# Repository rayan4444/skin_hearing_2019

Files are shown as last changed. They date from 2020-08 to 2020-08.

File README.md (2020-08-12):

# Skin Hearing PCB Repository

Altium files Repository for Skin Hearing project. The Main Board houses the microcontroller and options for audio inputs. The Flex Electrodes is a two-way configurable flex PCB for skin stimulating electrodes.

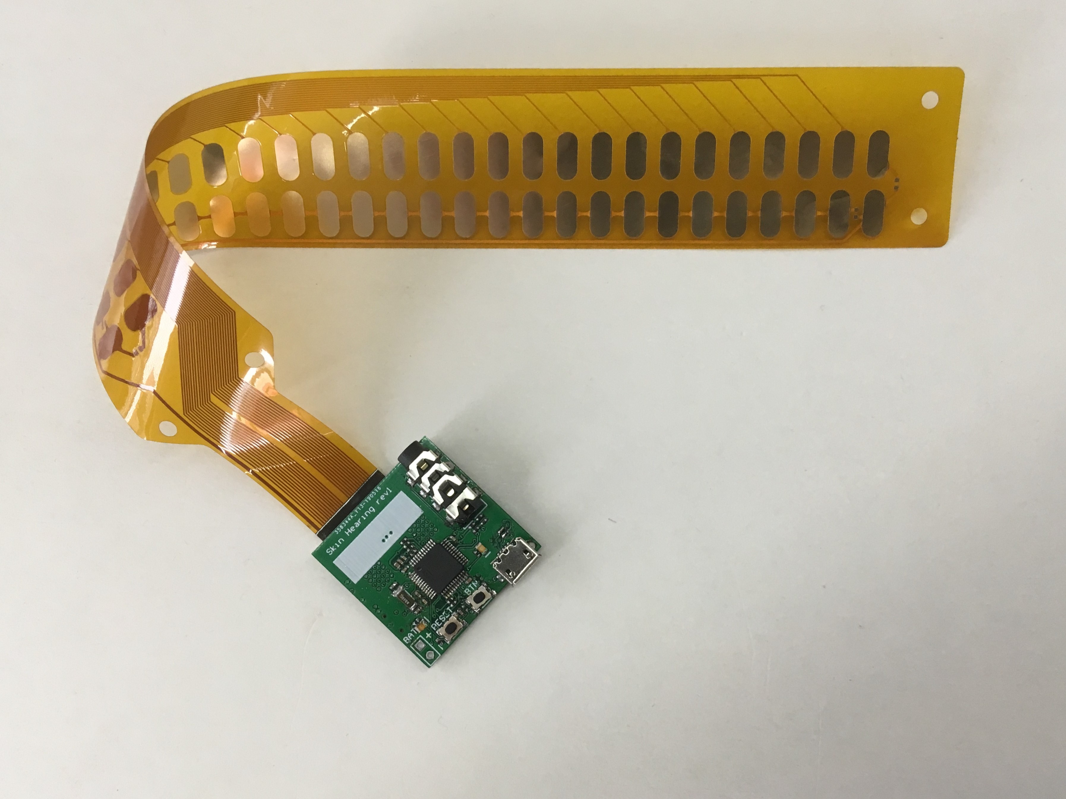
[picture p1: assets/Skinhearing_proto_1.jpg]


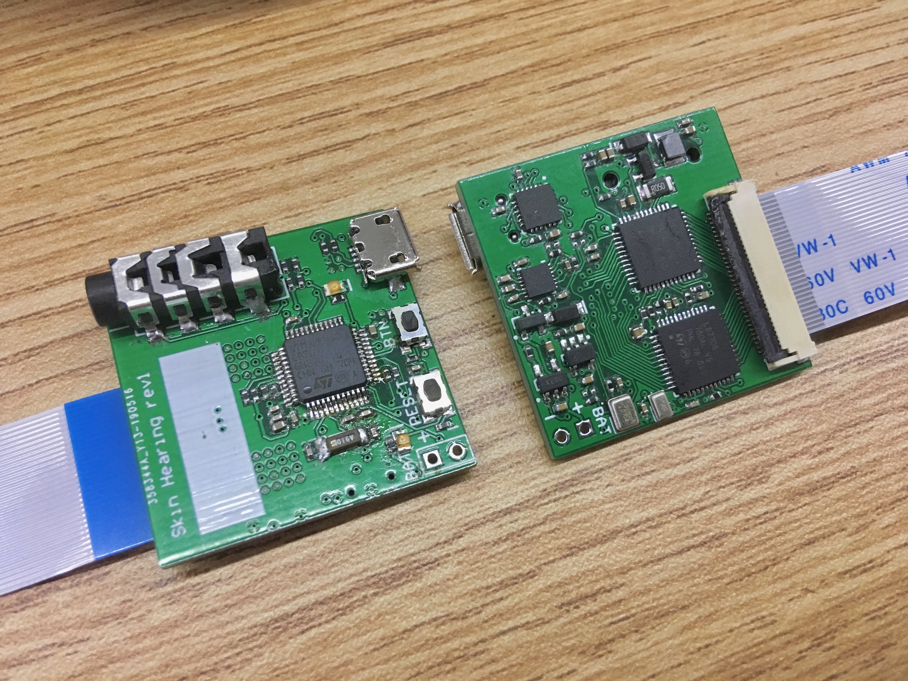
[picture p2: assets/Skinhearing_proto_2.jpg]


## Features
Main board: 4 Layers
* STM32F410 microcontroller
* 1x CP2104 USB-UART bridge
* 1x SPH0645LM4H-B Digital microphone
* 1x SPV1840LR5H-B Analog microphone
* 1x MAX9814 Audio amplifier
* 1x 3.5mm audio jack for external microphone
* 2x LED7708 LED drivers to control electrode current
* 1x 32pin FCC connector for electrodes
* 1x Button
* 1S Battery charger and LDO

Flex Electrodes:
* Configuration 1: solder 0Ω resistors on R3 and R2, leave R1 and R4 not populated
* Configuration 2: solder 0Ω resistors on R1 and R4, leave R2 and R3 not populated

## Connections and Pinout
STM32F410:

|Signal|Pin|Notes|
|:---:|:----:|:---:|
|USART1_TX|PA9|Programming|
|USART1_RX|PA10|Programming|
|Button|PA0||
|MIC_AMP|PB0|output of audio amplifier|
|I2S1_WS|PA4|digital mic|
|I2S1_CK|PA5|digital mic|
|I2S1_SD|PA7|digital mic|
|LE|PB12|LED driver|
|DCLK|PB13|LED driver|
|DOUT|PB14|LED driver|
|DIN|PB15|LED driver|
|GSSY|PA8|LED driver|
|XFLT|PA11|LED driver|
|IOK|PB5|LED driver|
|XVOK|PB6|LED driver|
|XOVF|PB7|LED driver|
|XMSK|PB8|LED driver|

## Programming instructions

1. Download and install [CP210x drivers](https://www.silabs.com/products/development-tools/software/usb-to-uart-bridge-vcp-drivers)
2. 	Make sure the BOOT config resitors are soldered properly to program over UART
BOOT0= HIGH, BOOT1=LOW
    * R18 and R23 soldered
    * R19 and R21 not populated
3. Get [STM32 flasher](https://www.st.com/en/development-tools/flasher-stm32.html) from the ST Website
4. Make sure your USB cable has communication wires!

## Firmware
Did not get consent to share

## Errata, fixes and debugging notes

#### Changes from rev 1.0
*	Removed R7 and R8 to improve USB reliability
* Corrected TX/RX connection on the CP2104 Chip
* Added Ground connections to the FPC connector
* Renamed channels to match the electrodes Flex PCB

#### Manufacturing notes
* Main board: 4L, 1.6mm thickness, 30x30mm

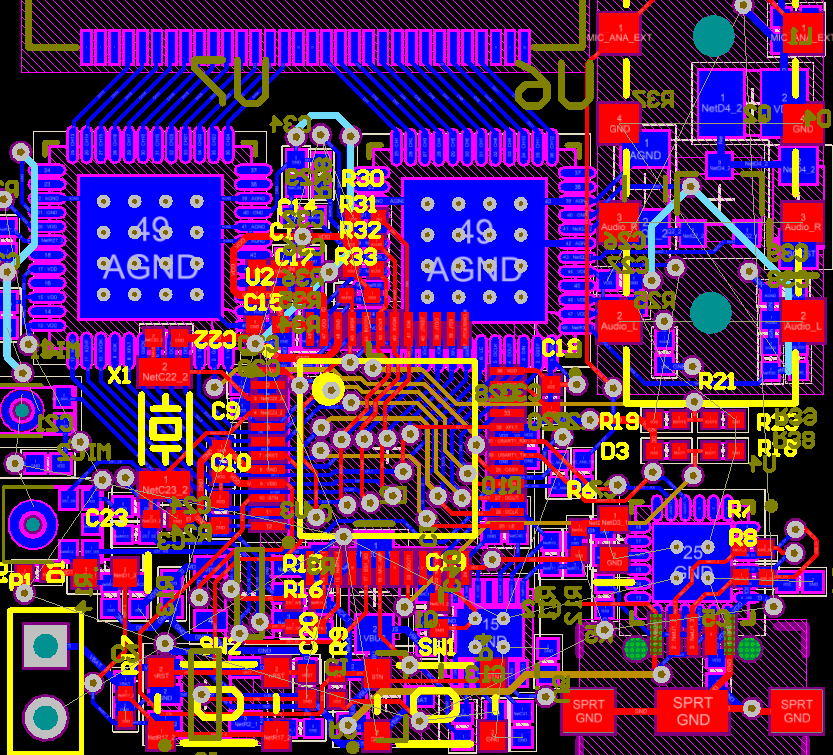
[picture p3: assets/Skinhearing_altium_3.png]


* Electrodes: FPC. See layer stack-up below

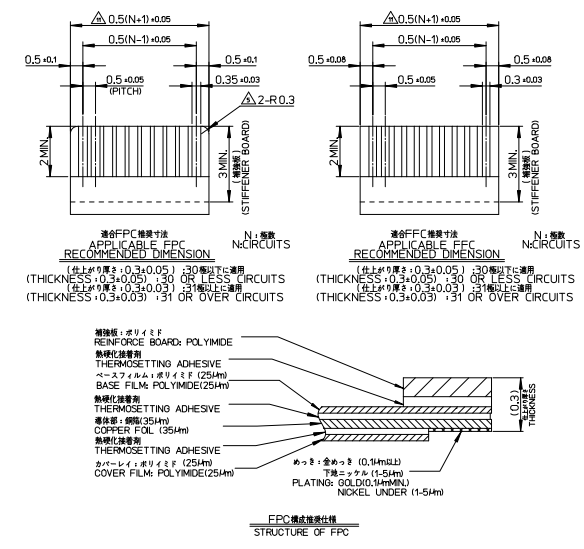
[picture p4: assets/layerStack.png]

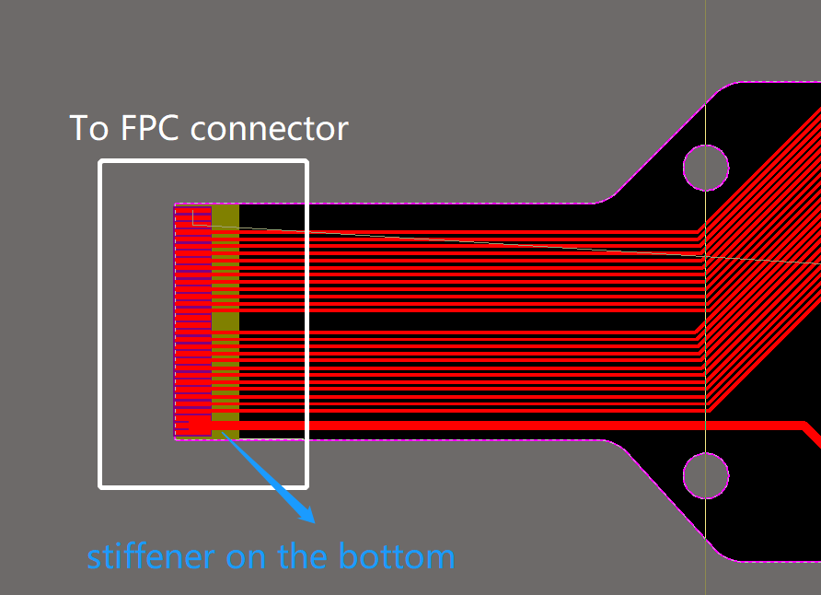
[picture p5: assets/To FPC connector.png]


#### Suggestions for future designs
*	Industrial design considerations: position of buttons, LED and connectors
* In case LED drivers produce discomfort: consider using a DAC and an improved Howland current pump to control the outputs to the electrodes.
* Remove redundant audio input source once you've tested all of them
* Consider communication with other devices: ex: Bluetooth

## Datasheets
* [LED7708](https://www.st.com/resource/en/datasheet/led7708.pdf)
* [MAX9814](https://datasheets.maximintegrated.com/en/ds/MAX9814.pdf)
* [STM32F410 - 48Pin](https://www.st.com/resource/en/datasheet/stm32f410cb.pdf)
* [SPV1840LR5H-B](https://www.knowles.com/docs/default-source/model-downloads/spv1840lr5h-b-rev-b-datasheet.pdf)
* [SPH0645LM4H-B](https://cdn-shop.adafruit.com/product-files/3421/i2S+Datasheet.PDF)
* [CP2104](https://www.silabs.com/documents/public/data-sheets/cp2104.pdf)

## References and Tutorials
* Examples for LED7708 firmware : [evaluation boards](https://www.st.com/content/st_com/en/products/evaluation-tools/solution-evaluation-tools/led-and-general-lighting-solution-eval-boards/steval-ill035v1.html#resource) and [software](https://www.st.com/content/st_com/en/products/evaluation-tools/solution-evaluation-tools/led-and-general-lighting-solution-eval-boards/steval-ill035v1.html#tools-software)
* [STM32F4 tutorials](http://stm32f4-discovery.net)

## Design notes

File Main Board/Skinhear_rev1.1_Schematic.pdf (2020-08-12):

# C11470nF C¹²

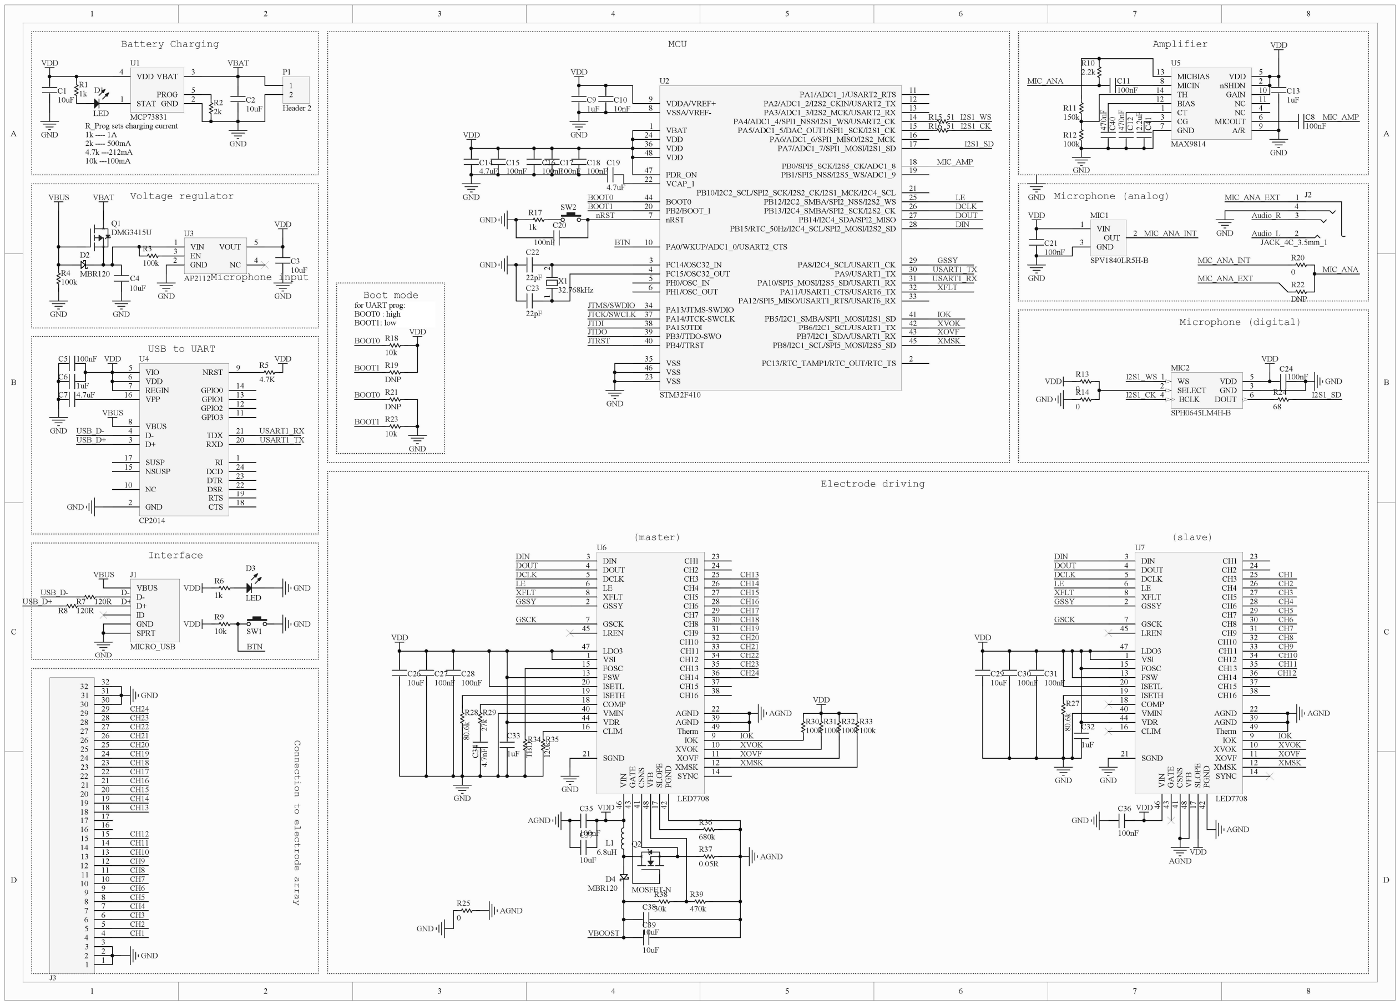
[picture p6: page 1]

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
### Battery Charging

### Voltage regulator

### Microphone input

### MCU

### Interface

STAT 1 | GND | 2
VBAT | 3 VDD 4
PROG | 5

U1

MCP73831

1k

R1

2k

R2 10uF

C1

10uF

C2

VDD | VBAT

GND

R_Prog sets charging current 1k ---- 1A
2k ---- 500mA
4.7k ---212mA
10k ---100mA

D1

LED

GND

1
2

P1

Header 2

10uF

C4

10uF

100k | C3

R3

GND

GND

GND

VDD

VBUS

100k

R4

GND

D2

MBR120

VBAT

Q1
DMG3415U
VIN 1

GND 2

EN 3
NC | 4
VOUT | 5

U3

AP2112

VBUS

GND

USB_D-USB_D+

RI 1

GND 2

D+ 3

D- 4

VIO 5
VDD 6
REGIN 7

VBUS 8

NRST 9

NC 10

GPIO3 | 11 GPIO2 | 12 GPIO1 | 13 GPIO0 | 14

NSUSP 15

VPP 16

SUSP 17

CTS | 18 RTS | 19
RXD | 20 TDX | 21
DSR | 22 DTR | 23 DCD | 24

U4

CP2014

1uF

C6

C7 4.7uF

C5 100nF

4.7K

R5

### USB to UART

VDD | VDD

GND

GND

R7 120R
R8 120R

USB_D-USB_D+

VBUS

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
VDD | GND

BTN

SW1

VBAT 1

PC13/RTC_TAMP1/RTC_OUT/RTC_TS 2

PC14/OSC32_IN 3
PC15/OSC32_OUT 4
PH0/OSC_IN 5
PH1/OSC_OUT 6

nRST 7

VSSA/VREF- 8

VDDA/VREF+ 9

PA0/WKUP/ADC1_0/USART2_CTS 10

PA1/ADC1_1/USART2_RTS | 11
PA2/ADC1_2/I2S2_CKIN/USART2_TX | 12
PA3/ADC1_3/I2S2_MCK/USART2_RX | 13
PA4/ADC1_4/SPI1_NSS/I2S1_WS/USART2_CK | 14
PA5/ADC1_5/DAC_OUT1/SPI1_SCK/I2S1_CK | 15
PA6/ADC1_6/SPI1_MISO/I2S2_MCK | 16
PA7/ADC1_7/SPI1_MOSI/I2S1_SD | 17
PB0/SPI5_SCK/I2S5_CK/ADC1_8 | 18
PB1/SPI5_NSS/I2S5_WS/ADC1_9 | 19

PB2/BOOT_1 20

PB10/I2C2_SCL/SPI2_SCK/I2S2_CK/I2S1_MCK/I2C4_SCL 21 VCAP_1 22

VSS 23

VDD 24

PB12/I2C2_SMBA/SPI2_NSS/I2S2_WS | 25
PB13/I2C4_SMBA/SPI2_SCK/I2S2_CK | 26
PB14/I2C4_SDA/SPI2_MISO | 27
PB15/RTC_50Hz/I2C4_SCL/SPI2_MOSI/I2S2_SD | 28
PA8/I2C4_SCL/USART1_CK | 29
PA9/USART1_TX | 30
PA10/SPI5_MOSI/I2S5_SD/USART1_RX | 31
PA11/USART1_CTS/USART6_TX | 32
PA12/SPI5_MISO/USART1_RTS/USART6_RX | 33
PA13/JTMS-SWDIO 34
PA14/JTCK-SWCLK 37
PA15/JTDI 38
PB3/JTDO-SWO 39
PB4/JTRST 40
PB5/I2C1_SMBA/SPI1_MOSI/I2S1_SD | 41
PB6/I2C1_SCL/USART1_TX | 42
PB7/I2C1_SDA/USART1_RX | 43

VSS 35

VDD 36

BOOT0 44

PB8/I2C1_SCL/SPI5_MOSI/I2S5_SD 45

VSS 46

PDR_ON 47

VDD 48

U2

STM32F410
GND

GND

JTMS/SWDIO
JTCK/SWCLK
JTDI
JTDO
JTRST
VDD | GND

4.7uF

C14

10nF

C10

4.7uF

C19

1uF

C9

VDD

100nF

C15
100nF

C16
100nF

C17
100nF

C18

BOOT0
BOOT1

BOOT0

BOOT1

BOOT0

BOOT1

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
Boot mode | 1 2 | X1
| | 32.768kHz

22pF

C22

22pF

C23

SW2
GND
1k
R17 | nRST

GND

BTN

USART1_TX
USART1_RX

100nF

C20

for UART prog:
BOOT0 : high
BOOT1: low | Microphone (digital)

### Microphone (analog)

### Amplifier

VDD

VDD

100nF

C24

68

R24

I2S1_WS
I2S1_CK

I2S1_SD

I2S1_CK | I2S1_SD
I2S1_WS | GND

R16 51

R15 51

VIN 1

GND 3

OUT 2

MIC1

SPV1840LR5H-B

VDD

GND

100nF

C21

GND | 3
DOUT | 6
VDD | 5

BCLK 4

SELECT 2 WS 1

MIC2

SPH0645LM4H-B

MIC_ANA_INT

1

3

2

4

J2

JACK_4C_3.5mm_1

MIC_ANA_EXT

GND Audio_L Audio_R

100nF

C8

0

R20

DNP

R22

MIC_ANA_EXT

MIC_ANA_INT

MIC_ANA

GND

100nF

GND

VDD

MIC_ANA

MIC_AMP

### Electrode driving

DIN
DOUT
DCLK
LE
XFLT
GSSY

GND

GND

100nF

C2880.6k

R28

# GND 27k

R29 4.7nFC³⁴ | 1uF
C33 | 120k
R35

100nF

C27
10uF

C26

100nF

C35 VDD

GSCK

VDD | TBD

R34

(master) | (slave)

DIN
DOUT
DCLK
LE
XFLT
GSSY

GSCK

AGND

IOK
XVOK
XOVF
XMSK

IOK
XVOK
XOVF
XMSK

AGND

100nF

C31
100nF

C30
10uF

C29

VDD

VDD

# GND⁸⁰.6k

R27

VSI 1

GSSY 2

DIN 3
DOUT 4
DCLK 5
LE 6

GSCK 7

XFLT 8

IOK | 9
XVOK | 10
XOVF | 11
XMSK | 12

FSW 13

SYNC 14

FOSC 15

CLIM 16 | SLOPE 17
COMP 18 | ISETH 19 | ISETL 20

SGND 21

AGND | 22
CH1 | 23
CH2 | 24
CH3 | 25
CH4 | 26
CH5 | 27
CH6 | 28
CH7 | 29
CH8 | 30
CH9 | 31
CH10 | 32
CH11 | 33
CH12 | 34
CH13 | 35
CH14 | 36
CH15 | 37
CH16 | 38
AGND | 39 VMIN 40 | CSNS 41 | PGND 42 GATE 43
VDR 44
LREN 45 | VIN 46
LDO3 47 | VFB 48
Therm | 49

U6

LED7708

VSI 1

GSSY 2

DIN 3
DOUT 4
DCLK 5
LE 6

GSCK 7

XFLT 8

IOK | 9
XVOK | 10
XOVF | 11
XMSK | 12

FSW 13

SYNC 14

FOSC 15

CLIM 16 | SLOPE 17
COMP 18 | ISETH 19 | ISETL 20

SGND 21

AGND | 22
CH1 | 23
CH2 | 24
CH3 | 25
CH4 | 26
CH5 | 27
CH6 | 28
CH7 | 29
CH8 | 30
CH9 | 31
CH10 | 32
CH11 | 33
CH12 | 34
CH13 | 35
CH14 | 36
CH15 | 37
CH16 | 38
AGND | 39 VMIN 40 | CSNS 41 | PGND 42 GATE 43
VDR 44
LREN 45 | VIN 46
LDO3 47 | VFB 48
Therm | 49

U7

LED7708

1uF

C32

100nF

C36 VDD

IOK
XVOK
XOVF
XMSK

DIN

DOUT

DCLK

LE

XFLT

100k

R30
100k

R31
100k

R32
100k

R33

VDD

30k

R38
470k

R39

10uF

C37

D4
MBR120

L1
6.8uH

Q2

MOSFET-N

0.05R

R37

680k

R36

10uF

C38

10uF

C39 GND | VBOOST Connection to electrode array | 2.2uF C⁴¹

2.2k

R10

CT 1

nSHDN 2

CG 3

NC | 4
VDD | 5
MICOUT | 6
GND 7

MICIN 8

A/R | 9
GAIN | 10
BIAS 12

MICBIAS 13

TH 14
NC 11

U5

MAX9814 ⁴⁷⁰nF C⁴⁰150k

R11

100k

R12

GND

1uF

C13

GND
0

R14 0

R13

0

R25
AGND

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
10 | 10 11 | 11 12 | 12 13 | 13 14 | 14 15 | 15 16 | 16 17 | 17 18 | 18 19 | 19 20 | 20 21 | 21 22 | 22 23 | 23 24 | 24 25 | 25 26 | 26 27 | 27 28 | 28 29 | 29 30 | 30 31 | 31 32 | 32

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
CH10

CH11

CH6

CH13

CH14

CH15

CH16

CH17

CH18

CH19

CH20

CH21

CH22

CH23

CH24

CH13
CH14
CH15
CH16
CH17
CH18
CH19
CH20
CH21
CH22
CH23
CH24

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
CH10
CH11
CH12

CH6

CH12

AGND | GND
AGND | AGND

AGND

GSSY

D-D+

GND

ID

D+

D-

VBUS

SPRT

J1

MICRO_USB

MIC_AMP

USART1_TX

USART1_RX

GND

GND

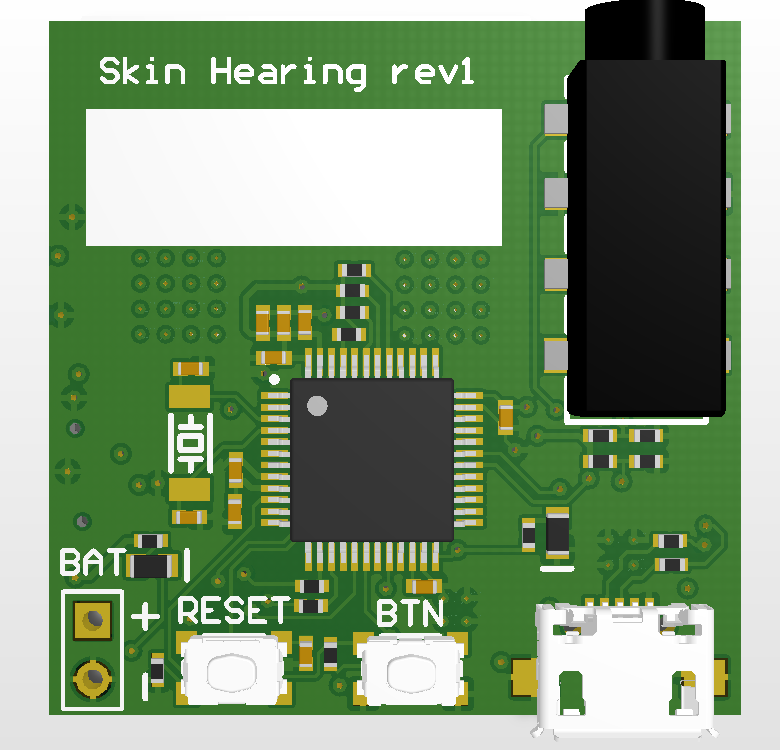
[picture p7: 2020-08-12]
assets/Skinhearing_altium_2.png

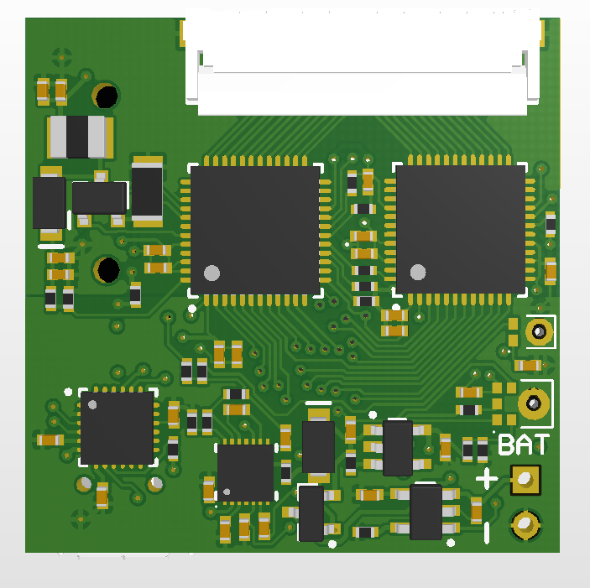
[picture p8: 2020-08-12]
assets/Skinhearing_altium_1.png
